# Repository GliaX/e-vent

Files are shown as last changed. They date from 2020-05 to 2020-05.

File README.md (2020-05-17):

# DISCLAIMER
This is an **INVESTIGATIONAL MEDICAL DEVICE** being evaluated for use
in hospital setting during **extreme crisis** leading to ventilator
shortages.

It has **not been approved** by any regulatory body.

It has significant potential for causing harm  even in the hands of
skilled and experienced clinicians. Any clinical application requires close
monitoring.

It is posted here in order to facilitate rapid knowledge sharing and research
on strategies for addressing the global ventilator shortage during pandemics.

Any of use of this device is done purely at your own risk and liability. The
developers and associated institutions do not accept any liability for its use.

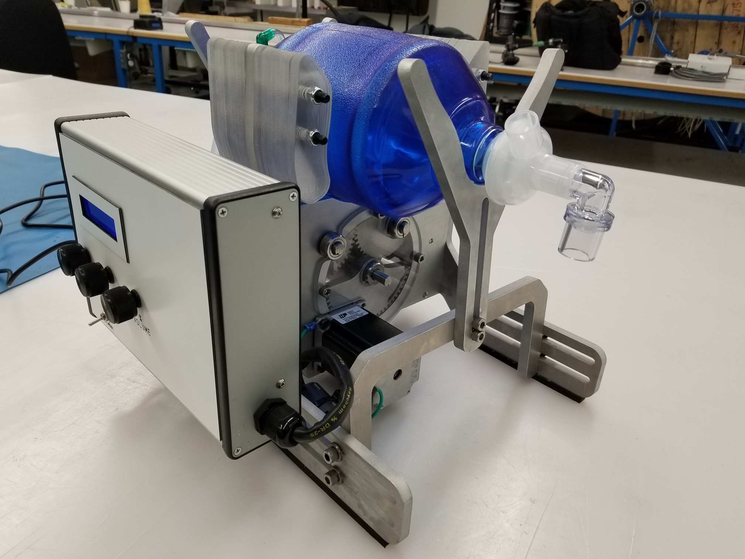
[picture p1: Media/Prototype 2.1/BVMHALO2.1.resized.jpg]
BVM-HALO-VENT-2.1


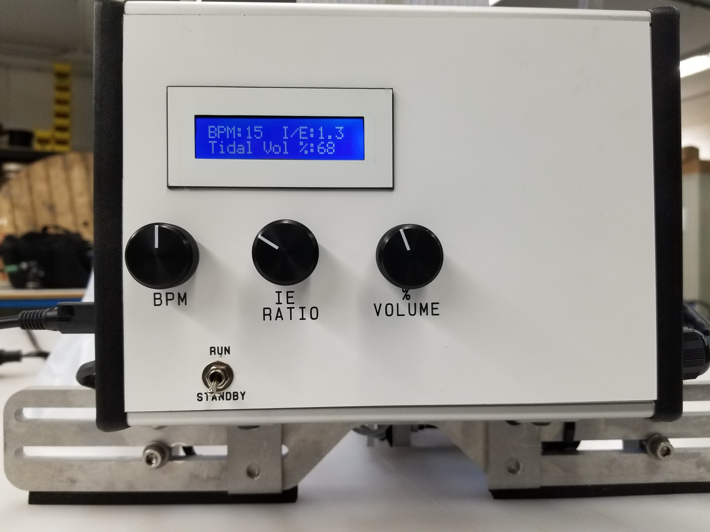
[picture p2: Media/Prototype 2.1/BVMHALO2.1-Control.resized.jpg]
BVM-HALO-VENT-2.1 controls


# BVM-HALO-Ventilator 2.1 Prototype Design Notes

## Control Architecture

### Microprocessor
An Arduino Uno was selected as the microprocessor controller primarily because of it’s abundant supply, ease of use and robustness. 

### Code
Custom code was written initially by UofT, rewritten by Promation and finally reviewed, revised and tested by Alithya (Matthew Humeny  - Matthew.Humeny@alithya.com). Note that there are some anomalies with the code that should be addressed in future revisions:

a) The limit switches were inadvertently soldered in at NC instead of NO. This was corrected using software. This should be reinstated as initially designed.

b) The rotation of the pots was reverse to correct the reverse electrical connection on the PCB. This should be correct on the PCB and the software

c) A 2nd order correction was added to the IE ratio to offset errors introduced due to the stepper losing steps at very high speeds. This needs to be fixed with hardware and software so that steps are not lost. Then the code can be reverted back as before

d) The plateau pause was reduced from 150mS to 50mS because it seemed the delay was longer than the software was set at, and it was not possible to measure the delay with the FluxMed. The plateau delay needs to be reinstated to 150 mS.

e) Although an alarm was connected, it was not programmed in. Alarming would be good to add.

f) The current code does not allow changing of bags that have a dramatic diameter difference from the Carestream BVM used at TGH. This feature can be easily added. 2 DIP switches (allowing for 4 different, DIP selectable bag diameters)

### Wiring and PCB
Initial wiring was designed and done by Promation using soldered and screw connections. The general electronic design was then incorporated into a custom PCB designed by Laveer Engineering (Jeff Hulcoop -  jhulcoop@laveer.ca). The current board has several fixes required (the 16 pin connector needs to be rotated 180deg., and the standby/run switch needs to be pulled to ground instead of +5V. The three pots are wired backwards [fixed with software))

### Power Supply
The entire unit is power by a Delta medical-grade power supply rated for 24VDC and 90W. This power supply has a robust locking plug which prevents removal without pulling back the plug jacket first (ie. tugging on the power cord will not disconnected it).

### LCD
The display used is a 2x16 LCD, although the device was initial designed for a 4x20 LCD. Subsequent versions should revert back to a 4x20 display which is easier to see and can display more information simultaneously.

### Shielding
Because of EMI generated onto the limit switch wires in Prototype #1, shielded 24AWG wiring was used for the two limit switches, and a shielded braided sleeve was placed over the stepper wires. The shielding for the stepper was grounded at both ends (to the stepper itself and to the control enclosure). A metal enclosure was selected intentionally to reduce noise. A large ferrite was added to the stepper motor wiring, and ferrites and capacitors were added on the PCB to reduce the effect of electrical noise. The stepper wiring and the limit switch wiring were kept apart to limit induced noise onto the limit switch wire.

### Stepper Controller
Electromate (Alex Werner - alex@electromate.com) worked with Applied Motion engineers to select and configure the appropriate industrial grade controller and stepper motor. The controller used is an STR4  (https://www.applied-motion.com/products/stepper-drives/str4). The controller is operating in 200 steps per rotation smooth.

### Stepper Motor
The industrial grade stepper motor is an Applied Motion HT23-601 (https://www.applied-motion.com/products/stepper-motors/ht23-601). It was connected in the bipolar parallel configuration, and the controller motor type was selected as type 8.

### Planetary Inline Gearbox
A 5:1 inline planetary gearbox was installed between the stepper motor and the device drive train to increase the delivered torque to the arms (see GAM PE-N23-005G Inline planetary gearbox ).

### Moisture Resistance
Some efforts were made to minimize the potential ingress of liquids into the enclosure and components. The potentioment shafts were sealed using rubber seals, and the LCD display was sealed with RTV sealant. The enclosure itself is relatively moisture resistant. With prolonged exposure to moisture, it is expected that electrical connections will corrode and this device will cease to operate properly. There is not concern about electrical shock because the device runs entirely on 24VDC, with a power consumption of well below 90W. The power supply itself is sealed and medical grade.

### Safety
This prototype device is guarded on both sides of the drive train with lexan shields, although pinch points do remain on this device. A resuscitator bag should never be installed or removed unless the arms are retracted and in the standby position, or if the power is physically disconnected from the device.

### Rebooting
In the unlikely case that the controller locks up, unplug the power supply from the device, and reconnect it. This will reset he microcontroller.

## Mechanical Design
The initial design was based on the MIT E-vent geared design. Prototype #1, like the MIT design, did not take into account the significant mechanical loading generated by the resuscitator when under full ventilating load (30BPM, 1:3.0 IE, 100% Vol, PEEP at 30cm H2O, 2 HEPA filters, plus the resistance/compliance of a test lung).

# Testing
Version 2.1 has undergone bench testing with a mechanical test lung as well as in-vivo animal testing. After REB approval, an 80Kg Yorshire Pig was fully anesthetized and ventilated for 2.5 hours at a range of settings: PEEP 0-10; VT 200-800 ml; RR 5-30. The device performed consistently over the full range of these settings. Effectiveness of ventilation was assessed by spirometer <a href="https://mbmed.com/fluxmed-grh/" rel="nofollow" target="_blank">Fluxmed GrH</a> and arterial blood gas monitoring. Testing data will be made available in the repository after review. 

The device has not been used clinically and there is thus no human data available.

# Development Team
The project was initiated in Toronto in April 2020 during the COVID-19 pandemic. It builds on the concept originally created by the MIT <a href="https://e-vent.mit.edu" rel="nofollow" target="_blank">E-Vent Team</a>. A collaboration between the 
<a href="https://apil.ca" rel="nofollow" target="_blank">Lynn and Arnold Irwin Advanced Perioperative Imaging Lab</a> at University Health Network,
<a href="https://www.promation.com" rel="nofollow" target="_blank">Promation</a>, 
<a href="https://www.engineering.utoronto.ca" rel="nofollow" target="_blank">University of Toronto Faculty of Applied Science & Engineering</a> and 
<a href="https://mi2health.com" rel="nofollow" target="_blank">Mackenzie Innovation Institute</a>

University Health Network: Azad Mashari, Jesse May, Maha Al-Mandhari, William Ng

University of Toronto: Kamran Behdinan, Ben Chan

Mackenzie Innovation Institute: Aviv Gladman

Promation: Darryl Spector, Steve Evans, Alex Sakuta, Adam Mitlyng, Harin De Mel, Yajurvin Govindraj, David Chakhnazarov, Manju Shivaswamy 

Laveer Engineering: Jeff Hulcoop 

Alithya: Matthew Humeny

Electromate: Alex Werner

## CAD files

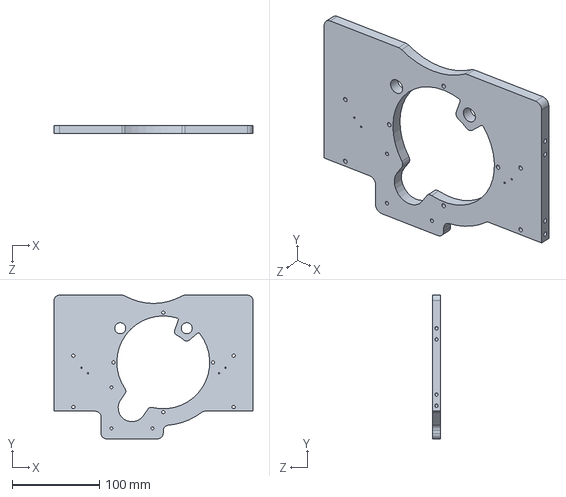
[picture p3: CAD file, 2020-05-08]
Mechanics/CAD Files - Solidworks/Promation - Main Plate.SLDPRT
228.6 x 165.1 x 9.53 mm

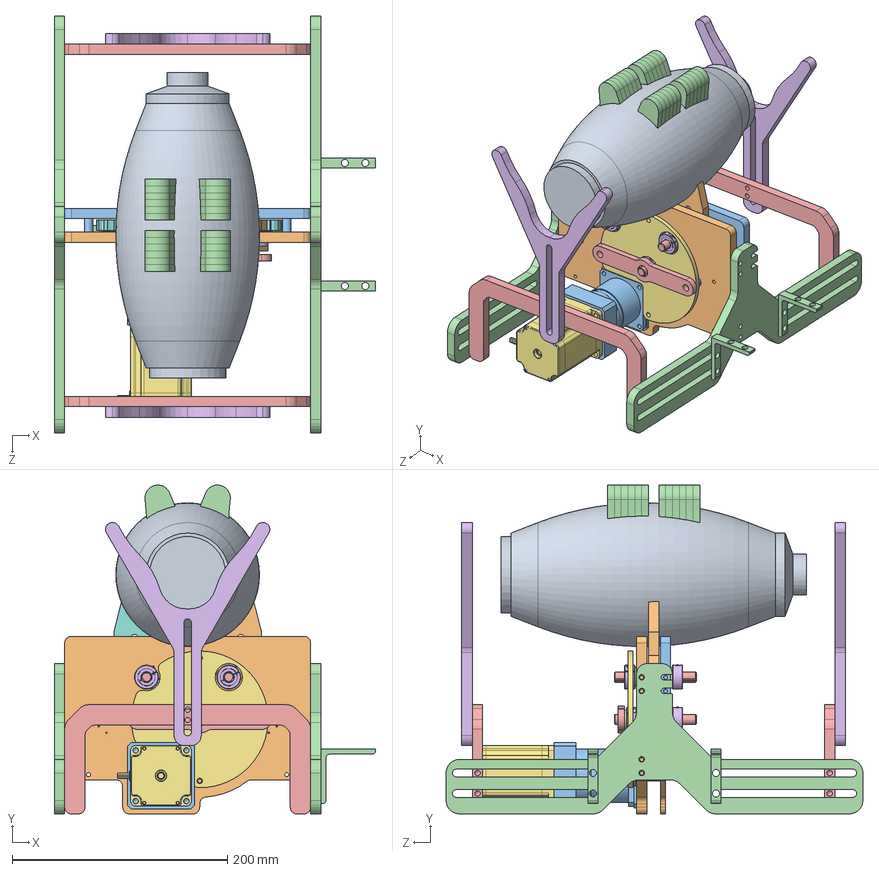
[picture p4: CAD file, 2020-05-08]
Mechanics/CAD Files - Solidworks/Promation Ventilator Assembly.SLDASM
298.5 x 305.6 x 387.4 mm
Main Plate
Front Plate
Bridge R1 x 2
Yoke Bracket R1 x 2
Yoke x 2
Applied Motion Products_HT23-601
Flag - Max Open x 2
Intermediate gear R1
Front Plate Guarding R1
MMC #92510A565_ALUM UNTHRD SPACER x 4
CP Bracket x 2
support
Washer - #10 - Modified x 4
McMaster # 1677K400_OIL-EMBEDDED FLANGED SLEEVE BEARINGS W PTFE x 7
Gearbox Spacer
McMaster_6325K130_8mm
McMaster_6325K110_modified
McMaster_5906K511 x 5
SS_5GL2T x 2
McMaster #7398K100_FULLY KEYED 304 STAINLESS STEEL DRIVE SHAFT x 3
McMaster #6435K330_ONE-PIECE CLAMP-ON SHAFT COLLAR x 6
Main Plate Guard R1
Drive Finger Opposite
Drive Finger Opposite_Teeth
Drive Finger
GAM_PE-N23-005G (NEMA 23, 0.250)
New Fingers_Design x 24

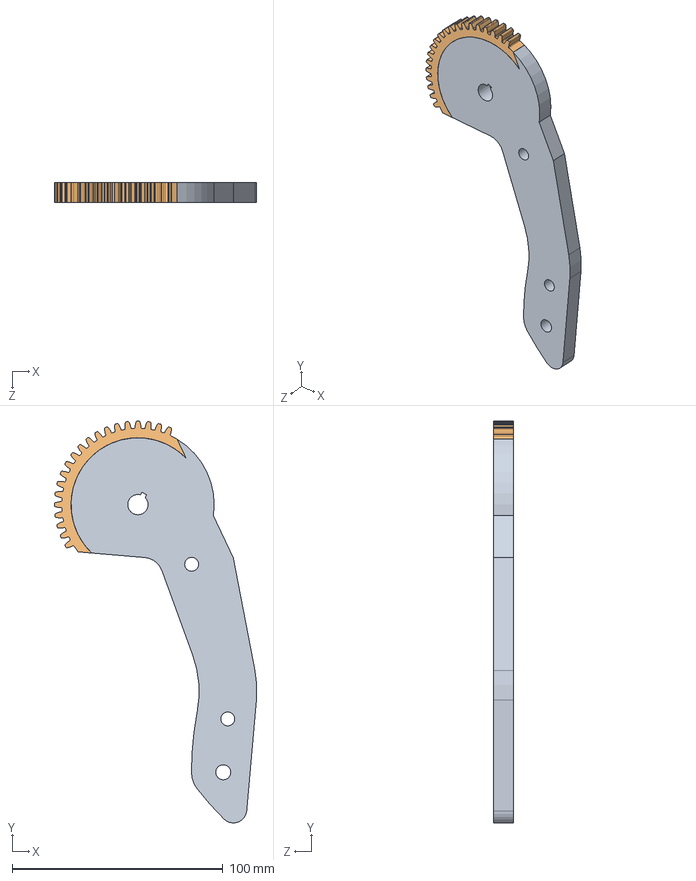
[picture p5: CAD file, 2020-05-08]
Mechanics/CAD Files - Solidworks/Promation - Drive Finger Opposite.SLDASM
96.1 x 190.7 x 9.53 mm
Drive Finger Opposite
Drive Finger Opposite_Teeth

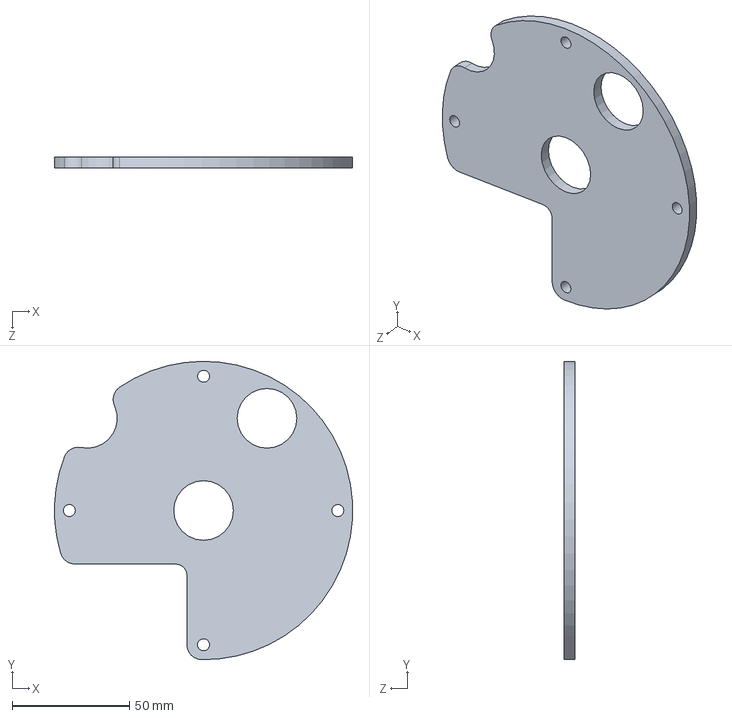
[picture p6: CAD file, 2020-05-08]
Mechanics/CAD Files - Solidworks/Promation - Main Plate Guarding.SLDPRT
126.8 x 127.0 x 4.76 mm

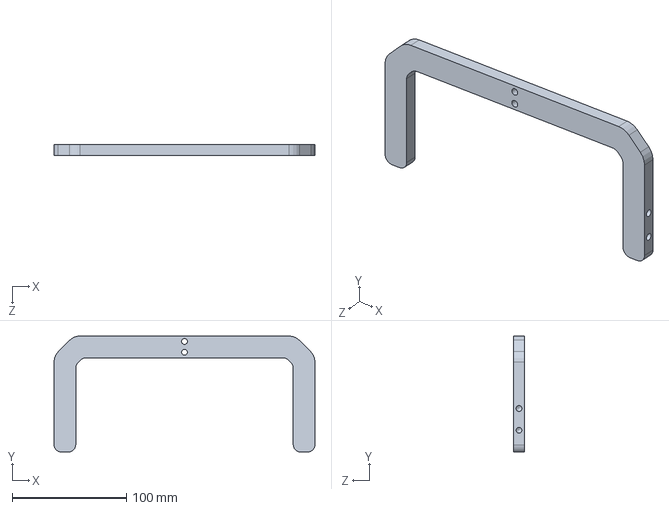
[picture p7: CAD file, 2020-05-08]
Mechanics/CAD Files - Solidworks/Promation - Bridge.SLDPRT
228.6 x 101.6 x 9.53 mm

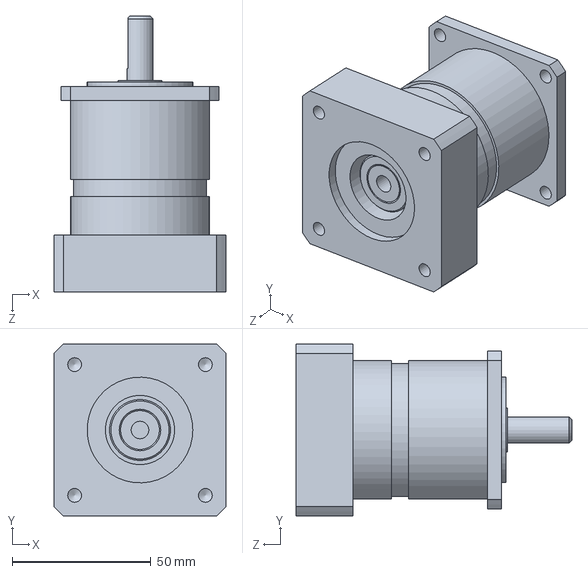
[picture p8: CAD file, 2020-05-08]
Mechanics/CAD Files - Solidworks/GAM_PE-N23-005G (NEMA 23, 0.250).SLDPRT
62.0 x 62.0 x 99.5 mm

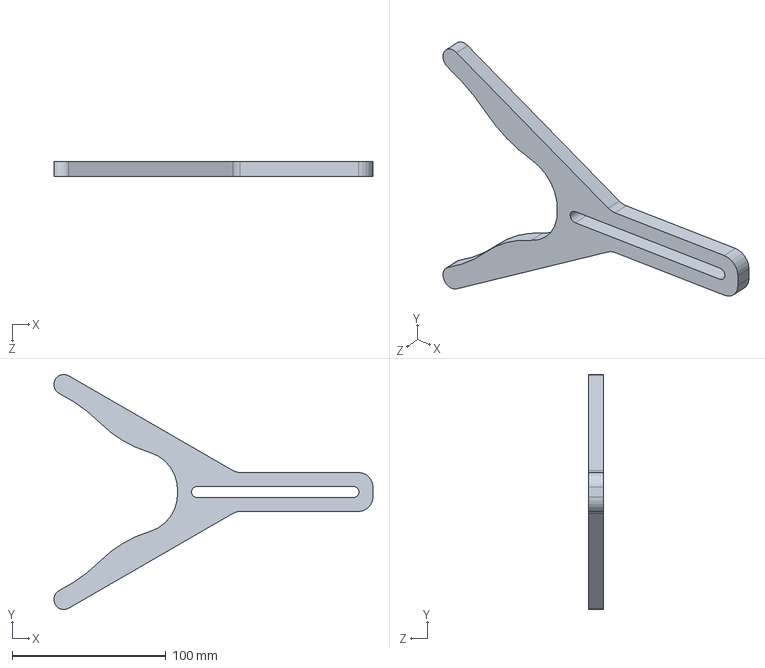
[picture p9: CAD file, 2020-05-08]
Mechanics/CAD Files - Solidworks/Promation - Yoke.SLDPRT
207.3 x 152.8 x 10.0 mm

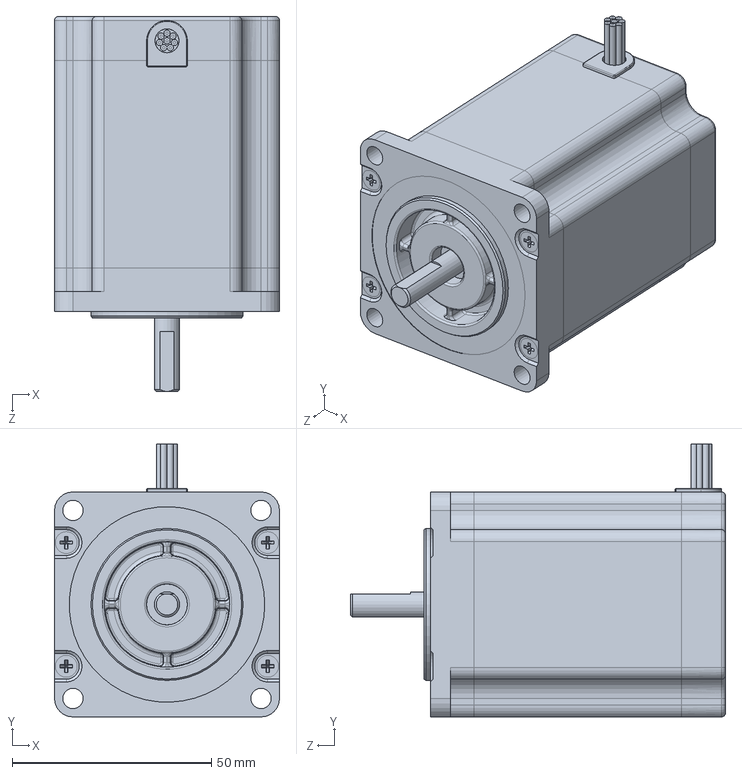
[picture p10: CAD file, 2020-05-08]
Mechanics/CAD Files - Solidworks/Applied Motion Products_HT23-601.SLDPRT
56.4 x 68.4 x 94.0 mm

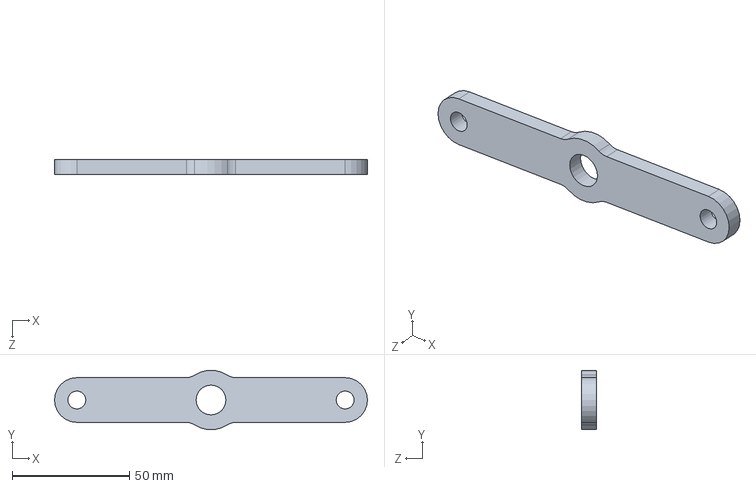
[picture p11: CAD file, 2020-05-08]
Mechanics/CAD Files - Solidworks/Promation - Shaft Support.SLDPRT
133.4 x 25.2 x 6.35 mm

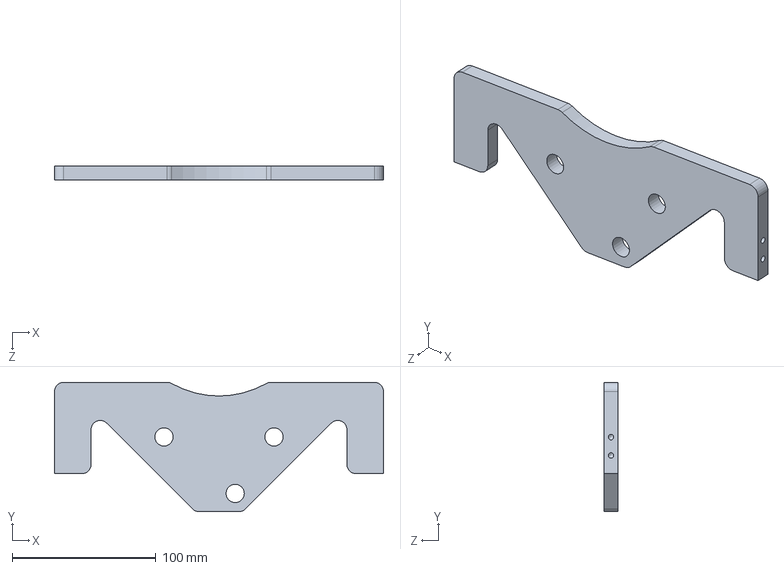
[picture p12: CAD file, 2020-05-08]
Mechanics/CAD Files - Solidworks/Promation - Front Plate.SLDPRT
228.6 x 89.9 x 9.53 mm

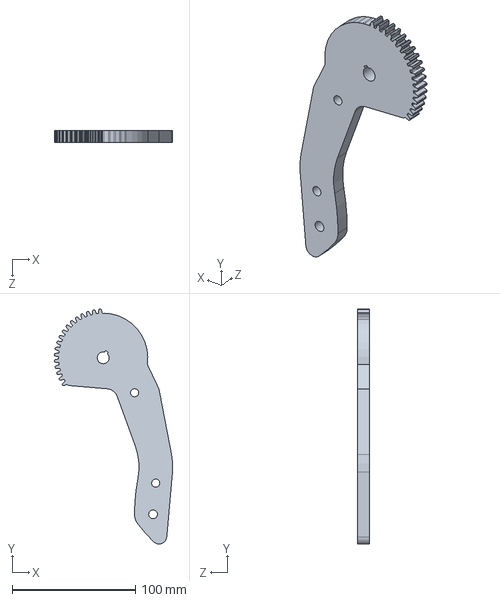
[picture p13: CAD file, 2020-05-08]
Mechanics/CAD Files - Solidworks/Promation - Drive Finger.sldprt
96.0 x 190.7 x 9.53 mm

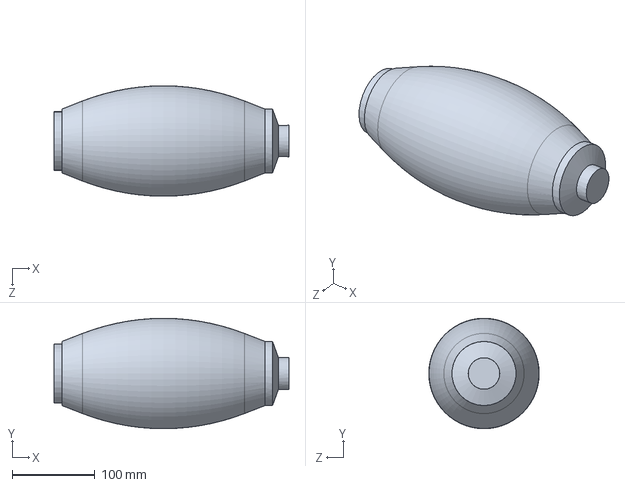
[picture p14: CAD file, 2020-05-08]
Mechanics/CAD Files - Solidworks/Ambu Spur II_Adult.SLDPRT
284.0 x 133.5 x 133.5 mm

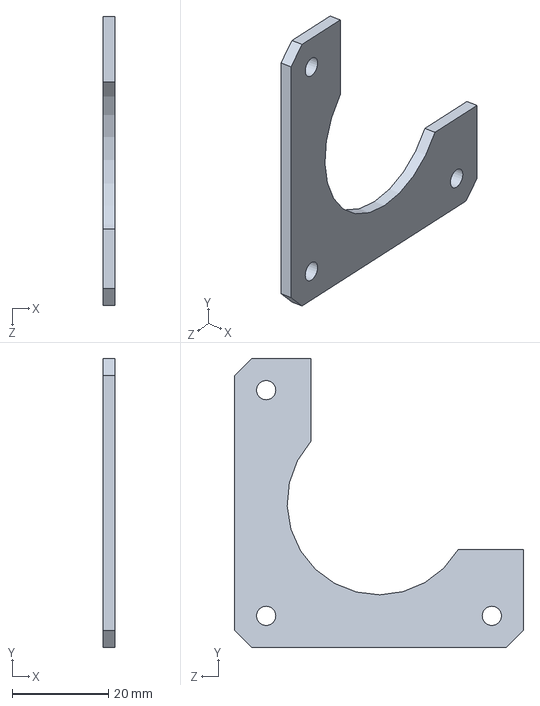
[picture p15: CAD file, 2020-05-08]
Mechanics/CAD Files - Solidworks/Promation - Gearbox Spacer.SLDPRT
2.54 x 60.0 x 60.0 mm

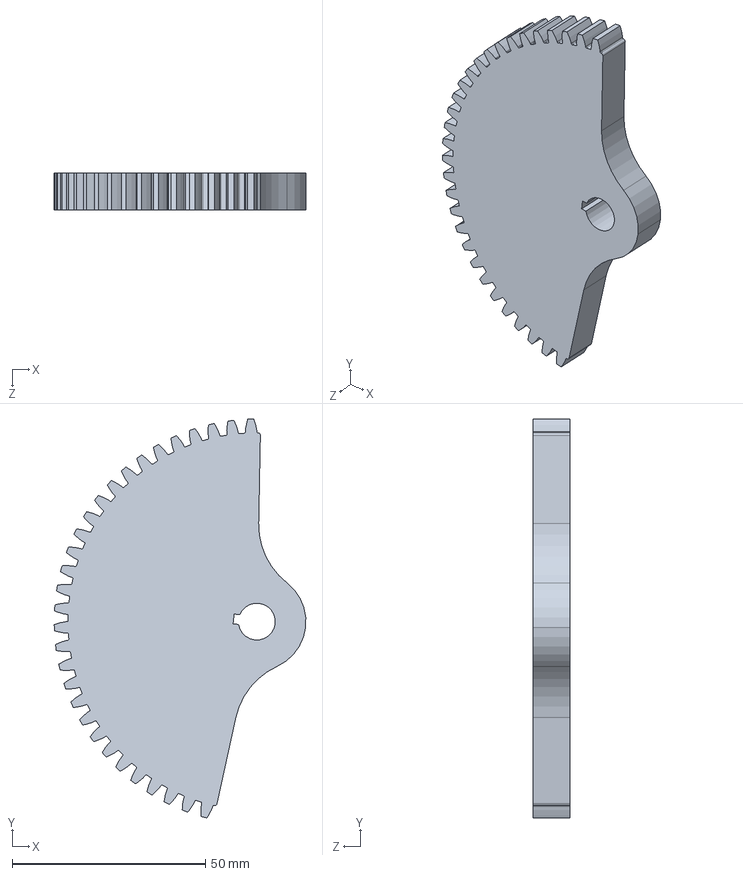
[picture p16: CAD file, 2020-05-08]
Mechanics/CAD Files - Solidworks/Promation - Intermediate gear.SLDPRT
65.0 x 103.1 x 9.53 mm

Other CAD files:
Mechanics/CAD Files - Solidworks/Promation - Control Box Support.SLDPRT
Mechanics/CAD Files - Solidworks/Promation - Finger Shoes.SLDPRT
Mechanics/CAD Files - Solidworks/Drive Finger Opposite.SLDPRT
Mechanics/CAD Files - Solidworks/Promation - Front Plate Guarding.SLDPRT
Mechanics/CAD Files - Solidworks/Digikey - SS_5GL2T.SLDPRT
Mechanics/CAD Files - Solidworks/Drive Finger Opposite_Teeth.SLDPRT
Mechanics/CAD Files - Solidworks/McMaster # 1677K400_OIL-EMBEDDED FLANGED SLEEVE BEARINGS W PTFE.SLDPRT
Mechanics/CAD Files - Solidworks/McMaster #6435K330_ONE-PIECE CLAMP-ON SHAFT COLLAR.SLDPRT
Mechanics/CAD Files - Solidworks/McMaster #7398K100_FULLY KEYED 304 STAINLESS STEEL DRIVE SHAFT.SLDPRT
Mechanics/CAD Files - Solidworks/McMaster_5906K511.SLDPRT
Mechanics/CAD Files - Solidworks/McMaster_6325K110_modified.SLDPRT
Mechanics/CAD Files - Solidworks/McMaster_6325K130_8mm.SLDPRT
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

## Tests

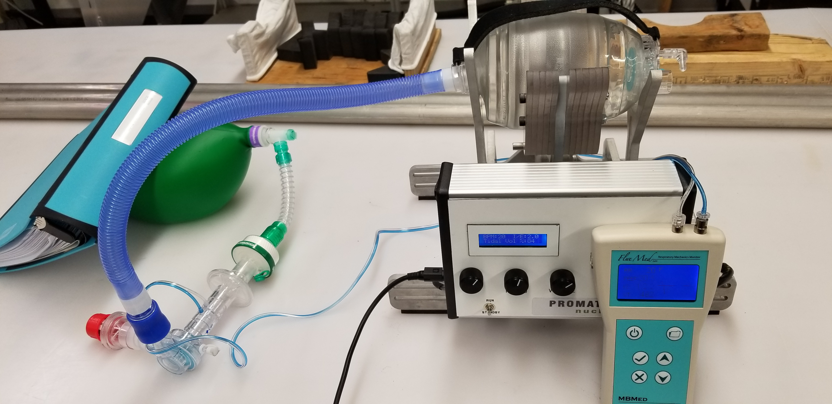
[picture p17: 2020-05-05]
Media/Prototype 2.1/BVMHALO2.1-Test Set-up 3-Mock Test Lung.jpg

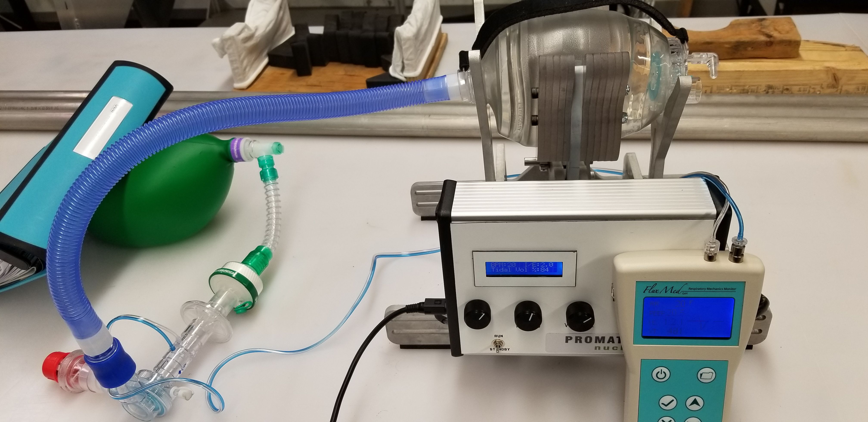
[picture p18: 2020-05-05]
Media/Prototype 2.1/BVMHALO2.1-Test Set-up 2.jpg

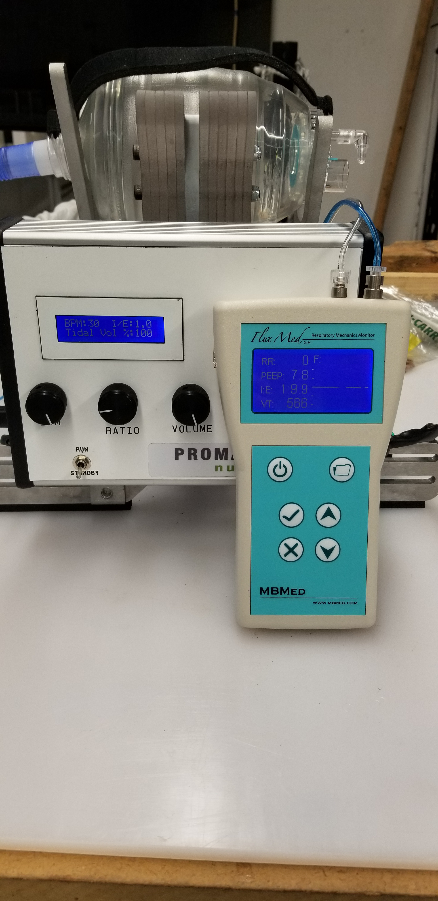
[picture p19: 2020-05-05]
Media/Prototype 2.1/BVMHALO2.1-Test Set-up 1.jpg

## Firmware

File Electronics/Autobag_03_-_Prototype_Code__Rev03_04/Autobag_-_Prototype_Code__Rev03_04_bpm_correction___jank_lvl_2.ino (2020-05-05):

//Include libraries
#include <Wire.h>
#include <LiquidCrystal.h>
#include <AccelStepper.h>

//Inputs
const int DIR = 9;                  // DIR on controller to pin 9 on arduino
const int STEP = 10;                // PUL on controller to pin 10 on arduino
const int LCD_RS = 12;              // LCD Register Select Signal on arduino pin 12
const int LCD_E = 11;               // LCD Operation Enable Signal on arduino pin 11
const int LCD_DB4 = 5;              // LCD Data Bus 4 Signal on arduino pin 5
const int LCD_DB5 = 4;              // LCD Data Bus 5 Signal on arduino pin 4
const int LCD_DB6 = 3;              // LCD Data Bus 6 Signal on arduino pin 3
const int LCD_DB7 = 2;              // LCD Data Bus 7 Signal on arduino pin 2
const int DIP_SW1 = 1;              // DIP Switch 1 on arduino pin 1
const int DIP_SW2 = 0;              // DIP Switch 2 on arduino pin 0
const int switchU = 6;              // Upper limit switch
const int switchH = 7;              // Home position in standby
const int startSwitch = 8;          // Start switch, latching
const int BPM = A0;                 // Desired bpm
const int Ratio = A1;               // Desired I/E ratio potentiometer (percentage of bag compression, from UofT code)
const int VolumeT = A2;             // Desired tidal volume of compression potentiometer

//Outputs
int buzzer = 13;                    //Buzzer 


// Constants - Variables to edit configurations below, you can tweak some settings here
const int LCD_COLS = 16;            // Number of columns on LCD display
const int LCD_ROWS = 2;             // Number of rows on LCD display
const float ACCEL = 50000.0;        // Acceleration and deceleration rate for stepper motor (steps per second per second)
const float MAXSPEED = 100000.0;     // Set the maximum allowable speed of the stepper motor (steps per second) This is set in setup() function and not used after that
const float HOMESPEED = 500.0;      // The speed for homing (steps per second)
const int delayBtwnInEx = 50;      //Changed value from 250 to 150// Delay between inspriration and expiration (milliseconds)
const int delayBtwnExIn = 20;       //Changed value from 250 to 20// Delay between expiration and inspiration (milliseconds)
const int cycleTmin = 5;            // Minimum allowable bpm
const int cycleTmax = 30;           // Maximum allowable bpm
const float tidalVmin = 50.00;      // Minimum compression percentage
const float tidalVmax = 100.00;     // Maximum compression percentage
const int ieRatiomin = 100;         // Minimum ratio of inspiration:expiration
const int ieRatiomax = 300;         // Maximum ratio of inspiration:expiration
const float maxStrokeFinger = 27.0; // Maximum allowable stroke of finger (degrees)
const float gearR = 16*5;             // Gear Ratio between stepper and finger, default is 16, including the gearbox is an additional *5
const float StepsPerRev = 200;     // Steps per revolution (setting on Applied Motion STR4 driver)
const bool useBlocking = false;     // Set to true to use blocking mode for inspiration/expiration
const long stepsAfterSW = 0.0;   // The number of steps after the expiration limit switch to wait to perform stop

// Initialize the LCD library with the number of interface pins
LiquidCrystal lcd(LCD_RS, LCD_E, LCD_DB4, LCD_DB5, LCD_DB6, LCD_DB7);

// Initialize AccelStepper, 1=Motor Driver
AccelStepper stepper = AccelStepper(1, STEP,DIR);

// Set-points
int cycleT = 0; //Cycle time duration set by user

// Timers
int cycleCount = 0; //Every 100 cycles, home

// Variables
float tidalVolume = 0;              // Tidal volume setpoint
int stepperStroke = 0;              // Commanded step count of stepper, calculated from tidalVolume
float ieRatio = 0;                  // inspiration:expiration set-point
bool estopLatch = false;            // Set E-stop to default off at bootup
float freq_in = 0;                  // Frequency for inspiration
float freq_ex = 0;                  // Frequency for expiration
int stepsCycle = 0;                 // number of motor steps per cycle 
long rotTime = 0.0;                 // Rotation time
float rotTime_in = 0.0;             // Rotation time of inspiration
float rotTime_ex = 0.0;             // Rotation time of expiration
long targetPos = 0.0;               // Target position calculated for inspiration and expiration
long cyclePos = 0.0;                // Position of cycle home (not used for position in this revision)
bool cyclePosSet = false;           // The cycle position has been set
long expTargetPos = 0.0;            // Target position after expiration limit switch
bool alarm = false;                 // Alarm status
float rotTime_in_corr = 0.0;
float rotTime_ex_corr = 0.0;


//Cycle watchdog
bool activeCycle = false;

void configureLCD() {
  lcd.begin(LCD_COLS, LCD_ROWS);                // initialize the lcd 
  lcd.home();                                   // go home
  lcd.clear();                                  // Clear LCD
}

void readInputs() {
    //Serial.println("Reading inputs"); // This will flood the Serial port; only use if debugging
    
    bool dip1 = digitalRead(DIP_SW1);
    bool dip2 = digitalRead(DIP_SW2);

    //***********Serial Debugging must be removed for the dip switches to work, the serial ports are on the
    //*********** same pins as the DIP switches
    if (dip1 && dip2) {             // For future use to add Tidal calculation manipulated by dip switches
      // DIP Switch 1 OFF and DIP Switch 2 OFF
      
    } else if (!dip1 && dip2) {
      // DIP Switch 1 ON and DIP Switch 2 OFF
      
    } else if (dip1 && !dip2) {
      // DIP Switch 1 OFF and DIP Switch 2 ON
      
    } else {
      // DIP Switch 1 ON and DIP Switch 2 ON
      
    }

    // replaced map() function with equations below. The Map() function only dealt with integers and the fractions were truncated. These equations are rounded before being converted to an integer to deal with noisy analog inputs
    cycleT = round(((float(abs(1023-analogReadAvg(BPM)))/1000.0) * float(cycleTmax - cycleTmin)) + float(cycleTmin)); //Reads the analog pot value and interpolates to the target range defined by the editable variables above. This can be bpm
    cycleT = constrain(cycleT, cycleTmin, cycleTmax);
    ieRatio = round(((float(abs(1023-analogReadAvg(Ratio)))/1000.0) * float(ieRatiomax - ieRatiomin)) + float(ieRatiomin));
    ieRatio = constrain(ieRatio, ieRatiomin, ieRatiomax) / 100.0;
    tidalVolume = round(((float(abs(1023-analogReadAvg(VolumeT)))/1000.0) * (tidalVmax - tidalVmin)) + tidalVmin);
    tidalVolume = constrain(tidalVolume, tidalVmin, tidalVmax) / 100.0;
    
    tidalVolume = constrain(tidalVolume, 0.0, 1.0);
      
    printSetpoints();
    stepsCycle = (tidalVolume * maxStrokeFinger * gearR ) * (StepsPerRev / 360.0); // motor steps per cycle 
    //Remap tidal volume to new floor ********Does this still need to be remapped?
    //tidalVolume = map(600,0,1000,70, tidalVmax)/100.00; //Remaps "50%" position of compression

    //Calculate cycle time parameters
    rotTime = (1000.0 * 60.0) / cycleT; // tone(pin, frequency, duration), where duration is in milliseconds 
    //rotTime_in = rotTime / (1 + ieRatio); Alexs fudge...replaced this line with one below, to correct for IE ratio error
    rotTime_in = rotTime / (1 + ((ieRatio)+(0.1*ieRatio*ieRatio)) - 0.7);
    rotTime_ex = rotTime - rotTime_in - delayBtwnInEx - delayBtwnExIn;    
    freq_in = stepsCycle * (1000.0 / rotTime_in); // frequency for compression stroke in Hz
    rotTime_in_corr = rotTime_in - (2*(freq_in/ACCEL));
    freq_ex = stepsCycle * (1000.0 / rotTime_ex); // frequency for compression stroke in Hz
    rotTime_ex_corr = rotTime_ex - (2*(freq_ex/ACCEL));
    freq_in = stepsCycle * (1000.0 / rotTime_in_corr);
    freq_in *= 1.09;
    freq_ex = stepsCycle * (1000.0 / rotTime_ex_corr); // frequency for compression stroke in Hz
    freq_ex *= 1.09;
}

// Averaging of analog input value
int analogReadAvg(int pin) {  //Stolen from UofT
  int analogSum = 0;
  for (int i = 0; i < 5; i++) {
    analogSum += analogRead(pin);
    delay(5);
  }
  return analogSum / 5;
}


void estop() { //Not implemented in this revision LCD cursor positions need to be adjusted to 2 columns with new LCD
    //digitalWrite(buzzer,HIGH);
    noTone(STEP);
    if (estopLatch == 0) {
      estopLatch = 1;
      lcd.clear();
      lcd.setCursor(3,1);
      lcd.print("ERROR DETECTED");
      lcd.setCursor(3,2);
      lcd.print("PLEASE REBOOT");
    }
}

// Debounces switchU, looks for 10 consecutive switch active readings
bool debounceswitchU()  
{
  static int isSwitchUActive = 0;               

  if (digitalRead(switchU) == 1) {
    isSwitchUActive++;
  } else {
    isSwitchUActive = 0;  
  }

  if (isSwitchUActive >= 25) {
    return 1;
  } else {
    return 0;
  }    
}

// Debounces switchH, looks for 10 consecutive switch active readings
bool debounceswitchH() 
{
  static int isSwitchHActive = 0;

  if (digitalRead(switchH) == 1) {
    isSwitchHActive++;
  } else {
    isSwitchHActive = 0;  
  }

  if (isSwitchHActive >= 25) {
    return 1;
  } else {
    return 0;
  }    
}

// Function to print setpoints to LCD
void printSetpoints() {                            
    lcd.clear();
    lcd.setCursor(0,0);
    lcd.print("BPM:");
    lcd.setCursor(4,0);
    lcd.print(cycleT);
    lcd.setCursor(8,0);
    lcd.print("I/E:");
    lcd.setCursor(12,0);
    lcd.print(ieRatio, 1);
    lcd.setCursor(0,1);
    lcd.print("Tidal Vol %:");
    lcd.setCursor(12,1);
    lcd.print(int(tidalVolume*100));
}

// Homing function to home microswitch
void homeStepper() {
  cyclePosSet=false;                                           // Clear the cycle position set when homing
  alarm = false;                                               // Reset alarm
  
  Serial.println("Homing Stepper");
  lcd.clear();
  lcd.home();
  lcd.print("Homing Stepper");

  // If already at the home postion move off the microswitch a half a revolution and then home
  if (digitalRead(switchH)){
    stepper.setMaxSpeed(HOMESPEED);
    stepper.runToNewPosition(stepper.currentPosition() + (StepsPerRev/2));
    //Serial.println("moving off switch");
  }
  
  //Home stepper to home microswitch
  stepper.moveTo(stepper.currentPosition() - 1000000000);      // set a value to run continuously
  stepper.setMaxSpeed(HOMESPEED);                              // set speed of move to the homing speed
  while (!debounceswitchH()) {                                 // run the stepper while there is no home switch active
    stepper.run();
    //Serial.println("moving home");  
  }
  stepper.stop();                                              //home switch is active, controlled stop
  stepper.runToPosition();                                     //position calculated for controlled stop
  stepper.setCurrentPosition(0);                               //zero postion
}

// Move to the cycle home postion, based on switchU micro switch
void moveCyclePos() {
  Serial.println("Moving to Cycle Posistion");
  lcd.clear();     
  lcd.home();
  lcd.print("Moving to");
  lcd.setCursor(0,1);
  lcd.print("Cycle Position");
  
  stepper.moveTo(stepper.currentPosition() + 1000000000);      // set a value to run continuously
  stepper.setMaxSpeed(HOMESPEED);                              // set speed of move to the homing spee
  
  while (!debounceswitchU()) {                                 // run the stepper while there is switchU is not active
    stepper.run();
  }
  
  stepper.stop();                                              // switchU is active, controlled stop
  stepper.runToPosition();                                     // position calculated for controlled stop
  cyclePos = stepper.currentPosition();                        // set cycle position
  cyclePosSet = true;                                          
  delay(1000);                                                 // added delay before operation of ventilator
}
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

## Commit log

2020-04-11 20200411 Update
    [Electrical BOM VENT.xlsx]
2020-05-05 Adding Images of Prototype 2.1
2020-05-08 Adding CAD Files
    [Ambu Spur II_Adult.SLDPRT, Applied Motion Products_HT23-601.SLDPRT, Digikey - SS_5GL2T.SLDPRT, Drive Finger Opposite.SLDPRT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]
